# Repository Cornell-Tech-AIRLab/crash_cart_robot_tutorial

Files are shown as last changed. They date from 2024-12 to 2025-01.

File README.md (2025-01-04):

# CRASH-CART-ROBOT-TUTORIAL-HRI 🤖

Crash Cart Robot Tutorial 

Healthcare workers face many challenges during bedside care that impede team collaboration and often lead to poor patient outcomes. Robots have the potential to support medical decision-making, help identify medical errors, and deliver supplies to clinical teams in a timely manner. However, there is a lack of knowledge about using robots to support clinical team dynamics despite being used in surgery, healthcare operations, and other applications. This version of the crash cart is a "Wizard of Oz" robot, allowing us to explore the robot's interactions with healthcare workers without needing to spend the time and resources to program it to run autonomously.

<p align="center"> 
 
</p>

This tutorial provides step-by-step instructions to build a low-cost cart robot with multimodal feedback capabilities using speech, drawer lights, and alerts to indicate the location of relevant supplies and task reminders.

See the Tutorial on [YouTube](https://www.youtube.com/watch?v=EV-0HwNPJiY).

Taylor, A., Tanjim, T., Sack, M., Hirsch, M., Cheng, K., Ching, K., St. George, J., Roumen, T., Jung, M., Lee, H. (2025) “Rapidly Built Medical Crash Cart! Lessons Learned and Impacts on High-Stakes Team Collaboration in the Emergency Room.” In Proc. of the 20th Annual ACM/IEEE Conference on Human Robot Interaction (HRI).

Taylor, A., Tanjim, T, Cao, H., Lee, H. “Towards Collaborative Crash Cart Robots that Support Clinical Teamwork.” In Proc. of the 19th Annual ACM/IEEE Conference on Human-Robot Interaction (HRI). *2024 Best Paper Honorable Mention*

<p align="center"> 
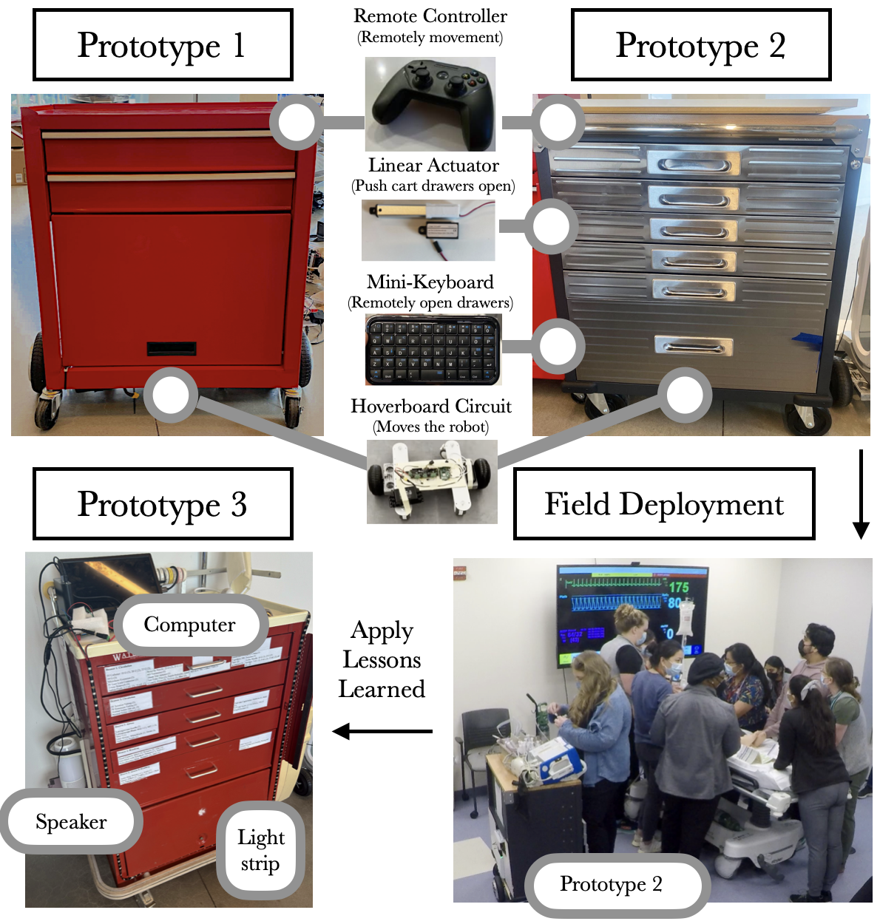
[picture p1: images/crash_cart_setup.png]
 

<b>Figure 1:</b> We built a series of teleoperated medical crash cart robots. Prototype 1 delivers supplies using a hoverboard circuit. Prototype 2 also delivers supplies, recommends supplies using drawer opening capabilities, and was deployed at a medical training event which revealed insights which led to the design of Prototype 3 that communicates recommendations and reminders using drawer lights, speech, and alerts.

</p>

## System Requirements
- Ubuntu 22.04.4 LTS (64-BIT)
- Python 3
- Robot Operating System 2 (Humble Distribution)

Contents: 
- [Introduction](#introduction) 
- [Materials and Supplies](#materials_supplies) 
- [Medical Crash Cart Robot Tutorial Steps](#medical_crash_cart_robot_tutorial_steps) 

## Introduction

Designing robots to support high-stakes teamwork in emergency settings presents unique challenges, including seamless integration into fast-paced environments, facilitating effective communication among team members, and adapting to rapidly changing situations. While tele-operated robots have been successfully used in high-stakes domains such as firefighting and space exploration, autonomous robots that aid high-stakes teamwork remain underexplored. To address this gap, we conducted a rapid prototyping process to develop a series of seemingly autonomous robot designed to assist clinical teams in the Emergency Room. We transformed a standard crash cart—which stores medical equipment and emergency supplies into a medical robotic crash cart (MCCR). The MCCR was valuated through field deployments to assess its impact on team workload and usability, identified taxonomies of failure, and refined the MCCR in collaboration with healthcare professionals. Our work advances the understanding of robot design for high-stakes, time-sensitive settings, providing insights into useful MCCR capabilities and considerations for effective human-robot collaboration. By publicly disseminating our MCCR tutorial, we hope to encourage HRI researchers to explore the design of robots for high-stakes teamwork.

You can use this bibtex to cite this work ([Taylor et al.](https://www.angeliquemtaylor.com/), 2025): 

``` 
@article{taylor_2025, 
author = {Taylor, A., Tanjim, T., Sack, M., Hirsch, M., Cheng, K., Ching, K., St. George, J., Roumen, T., Jung, M., Lee, H.}, 
title = {Rapidly Built Medical Crash Cart! Lessons Learned and Impacts on High-Stakes Team Collaboration in the Emergency Room.}, 
journal = {In Proc. of the ACM/IEEE Conference on Human Robot Interaction (HRI).}, 
year = {2025}
}
```

## Materials and Supplies

The parts list includes required supplies, price, quantity, and a link to a recommended source. You likely already own most items. The total cost of the supplies is $417.

The battery pack is optional; two wall outlets serves as an alternative. A Linux laptop computer is required.

<b>Table 1:</b> Equipment List

| Item                                     | Price         | Quantity      | URL           |
| ---------------------------------------- | ------------- | ------------- | ------------- |
| Raspberry Pi 4  (At least 4 GB)          | $55.00        | 1             | [Amazon](https://www.adafruit.com/product/4296)  |
| Individually addressable LED light strip | $17.99        | 1             | [Amazon](https://www.amazon.com/VISDOLL-Individually-Addressable-Flexible-Controller/dp/B0CPLS16JL/ref=sr_1_4_sspa?dib=eyJ2IjoiMSJ9.TsHmF-lRIoGBvYJC14yH76SiGa3kCQYP1z9MJw8sPbFHuxxiVUnvk2_fiU6mu656BQlq5KbTNHeb5_LumQcb0X0OYDHDtCJN_rwwuf5z-v3bWnlL3Cn5DcHwlOG_Mdx9sP37ajw4Ocg3C4Y7M3PlQIEP1Z9yZiresYGvkUS-f6ggZ01eL3WeGkKSrfykM7fkyz9CT9XE3tvYreNPs_VAVzMoKI3IduZyyRaUuZjE2DB9uh-IXvjCOFOB-BNWAV8X9jAMOFD0EhvupdupGt4MgoGf1YjCXj0orK1jpqZbRBg.J0vCnA8CnLhwxM7LNrnHI55PK87y2msPtlu4ZD3rIlE&dib_tag=se&hvadid=174243246868&hvdev=c&hvlocphy=9004331&hvnetw=g&hvqmt=e&hvrand=15947800415004845809&hvtargid=kwd-87871454332&hydadcr=29841_9846530&keywords=ws2812b%2Bled%2Bstrip&qid=1711394444&sr=8-4-spons&sp_csd=d2lkZ2V0TmFtZT1zcF9hdGY&th=1)  |
| Keyboard (Connects to USB A)             | $2.00         | 1             | [Amazon](https://www.staples.com/nxt-technologies-keyboard-black-nx60880/product_24517816?cid=ps:gs:dot:nb:pmax:transtech&gad_source=1&gclid=CjwKCAjwzIK1BhAuEiwAHQmU3t1JYTTmAYI_HaWwEZnc8uMsLGvTyHrGdflbFACUAaloaU-xJKD52BoCmyQQAvD_BwE)  |
| Mouse (Connects to USB A)                | $2.71         | 1             | [Amazon](https://www.staples.com/nxt-technologies-wireless-optical-usb-mouse-black-nx60885/product_24517815?cid=ps:gs:dot:nb:pmax:transtech&gad_source=1&gclid=CjwKCAjwzIK1BhAuEiwAHQmU3k907qJZk150g8lUc_bgR_WLXvN4HjRAyOvO-Sm72jIvwHWpznKH6xoCgBsQAvD_BwE)  |
| Monitor (With either a VGA or HDMI port) | $25.25        | 1             | [Amazon](https://www.aliexpress.us/item/3256807264652139.html?src=google&src=google&albch=shopping&acnt=708-803-3821&slnk=&plac=&mtctp=&albbt=Google_7_shopping&gclsrc=aw.ds&albagn=888888&ds_e_adid=&ds_e_matchtype=&ds_e_device=c&ds_e_network=x&ds_e_product_group_id=&ds_e_product_id=en3256807264652139&ds_e_product_merchant_id=552411188&ds_e_product_country=US&ds_e_product_language=en&ds_e_product_channel=online&ds_e_product_store_id=&ds_url_v=2&albcp=19623912707&albag=&isSmbAutoCall=false&needSmbHouyi=false&gad_source=1&gclid=Cj0KCQjw5ea1BhC6ARIsAEOG5pw0ThUU9ioUfy6q8Gpse0W5nCPYEZ5PL07aNTyMMek56Z9WtTKV-4waApLREALw_wcB&aff_fcid=041117238ac34ce9b29ae2ed38ab0a0f-1723474136729-08015-UneMJZVf&aff_fsk=UneMJZVf&aff_platform=aaf&sk=UneMJZVf&aff_trace_key=041117238ac34ce9b29ae2ed38ab0a0f-1723474136729-08015-UneMJZVf&terminal_id=415d44ae0b35443094f91ea630333c9f&afSmartRedirect=n&gatewayAdapt=glo2usa)  |
| Bluetooth speaker                        | $15.99        | 1             | [Amazon](https://www.amazon.com/Portable-Bluetooth-Wireless-Surround-Waterproof/dp/B08HKCH6HC/ref=asc_df_B08HKCH6HC/?tag=hyprod-20&linkCode=df0&hvadid=692875362841&hvpos=&hvnetw=g&hvrand=2035686413955776000&hvpone=&hvptwo=&hvqmt=&hvdev=c&hvdvcmdl=&hvlocint=&hvlocphy=9004331&hvtargid=pla-2281435180218&mcid=9e425a680a003b76bc8e3d1397160958&hvocijid=2035686413955776000-B08HKCH6HC-&hvexpln=73&gad_source=1&th=1)  |
| Male to female jumper wires              | $6.99         | 1             | [Amazon](https://www.amazon.com/Solderless-Multicolor-Electronic-Breadboard-Protoboard/dp/B09FP9M5J9/ref=sr_1_2_sspa?crid=285C9TEGW2OJE&dib=eyJ2IjoiMSJ9.6VrCXmlMYCYNvuTQX0vT18ycELHgXZXH9PN0oF4VWQdYk4psYj3UzBNkfVIU8OGZ4mi6Mo66XAKnZA7u0Idopb1NmCyKOZhnBhflIQloKcexdfN8Pxpzk5lSIB-XAtNZSnyTX9r9DEAhOVGiZ5ZN8bzyPb0FbIHclzaA-1-1LsXY3Z9E09I9gJSt13tY6p-ACQQbBvWMOF_940mtSjbySvwlDZREkQ4u65cgVEOfTxl9d-W6tyIptaniU_1eosEHJ_1_9GOZfSxJW9_Jn-fwQ8O1kt3PL9NwbfX-Acj7T38.bWZbX1JaxNVCQuquF9v3bd_YDqoABrhuUTLX3eYxoZk&dib_tag=se&keywords=long%2Bm%2Bto%2Bf%2Bjumper%2Bwire&qid=1722005738&s=industrial&sprefix=long%2Bm%2Bto%2Bf%2Bju%2Cindustrial%2C503&sr=1-2-spons&sp_csd=d2lkZ2V0TmFtZT1zcF9hdGY&th=1)  |
| Micro USB to HDMI or VGA                 | $7.99         | 1             | [Amazon](https://www.amazon.com/Converter-Compatible-Pictures-High-Definition-Monitor/dp/B09WMFKWYV/ref=asc_df_B09WMFKWYV/?tag=hyprod-20&linkCode=df0&hvadid=692875362841&hvpos=&hvnetw=g&hvrand=11251120234702158002&hvpone=&hvptwo=&hvqmt=&hvdev=c&hvdvcmdl=&hvlocint=&hvlocphy=9004331&hvtargid=pla-2281435177138&psc=1&mcid=906f684308503291bb8d74a65cd6fac0&hvocijid=11251120234702158002-B09WMFKWYV-&hvexpln=73&gad_source=1)  |
| USB C to power                           | $12.99        | 1             | [Amazon](https://www.amazon.com/Adapter-Charger-Charging-Compatible-Remarkable/dp/B09GYB2YG8/ref=asc_df_B09GYB2YG8/?tag=hyprod-20&linkCode=df0&hvadid=692875362841&hvpos=&hvnetw=g&hvrand=15632892786989388826&hvpone=&hvptwo=&hvqmt=&hvdev=c&hvdvcmdl=&hvlocint=&hvlocphy=9004331&hvtargid=pla-2281435182178&psc=1&mcid=8cc13fd8b3633d4c9d1ade48fa8707fa&hvocijid=15632892786989388826-B09GYB2YG8-&hvexpln=73&gad_source=1)  |
| Micro SD Card (At least 32 GB)           | $9.17         | 1             | [Amazon](https://www.amazon.com/dp/B073JWXGNT/ref=twister_B08CLNX58K?_encoding=UTF8&th=1)  |
| SD to USB adapter                        | $5.99         | 1             | [Amazon](https://www.amazon.com/Reader-Laptop-Windows-Chrome-RS-MMC/dp/B0C81FW814/ref=asc_df_B07MK99R14/?tag=hyprod-20&linkCode=df0&hvadid=692875362841&hvpos=&hvnetw=g&hvrand=5558208569019396501&hvpone=&hvptwo=&hvqmt=&hvdev=c&hvdvcmdl=&hvlocint=&hvlocphy=9004331&hvtargid=pla-2281435178778&mcid=b200ad31022538c49f855bc14aa1af93&hvocijid=5558208569019396501-B07MK99R14-&hvexpln=73&gad_source=1&th=1)  |
| Portable Power Station (optional)        | $249.99       | 1             | [Amazon](https://www.amazon.com/Anker-Portable-Generator-Traveling-Emergencies/dp/B0D62GMQ3F/ref=sr_1_1?crid=3OQSZ4QJ8UH6U&dib=eyJ2IjoiMSJ9.tGQ-J5haxYTAwL1awybF7r5b77QzjHUV5L4DpdkEKx9327o1Ri0o_fAo0fHeau_H_mCO-QfKyUxtNJJXKOpWLSvHvortJRIqT5scaOl5mlmgb0ho0jWMixqvxFlyN4EEjfWuSRUjDf8qWkElX4z0CoGpGwvA4_LAjuRklcHMRCFmmos63CCWAYLKFk4nqihG.nzRxaNY_JeZWl6dEtIdO0v09trXHNOOJdBqo8NcMjJU&dib_tag=se&keywords=anker+solux+c300x&qid=1734398531&sr=8-1)  |
| Scissors       | $4.24       | 1             | [Amazon](https://www.amazon.com/Scotch-1448-Precision-Scissor-8-Inches/dp/B001BKHHGS/ref=sr_1_5?crid=3V6SGIOQY7GU7&dib=eyJ2IjoiMSJ9.AjnComGyJnnJDRxxKFsxrNZHsMajCroUmd9qmX9nwIOeL8NUWILLhf7m7GxhVHXJnSHxpMeviTaEr2LnuPAxmw40hzl5Rdf_Owijw15Fy58SLyvQSLHSMel_WyEC4AQZjH3Wt3JMTi1D037q23B5Cp1LPqoWigxGkm8_nxsQEbk3pv5QtdriHM7wb_MSsVRWeJwYsnVV2mQhtSZmZ_oRn224Hzd6j-kkbbp2dRziO-LeHCFQFuRcWnOHuxAPROuZ2WCSZpSRmqLKDERhPR45x7LS81Nw6ncDYR1A48UJBUrHKtb-hRQ5I1Oo6R-ewswABJY6XRysK8yfr27H418VAKIqyyR3SABpj_s_BKoh9HcsGG-t7I9cEZCXVo_tpq80HNKd30ano7Ue8xTeSEQm9efUqQki64hn65fJhfFTHbI2lMVCrg_3kpbujX3iycB5.C85nwNh6hfaxJT_z_jb20ZgRAuvMlOfdWmmTRzfnOW0&dib_tag=se&keywords=scissors&qid=1735255473&sprefix=scissors%2Caps%2C189&sr=8-5)  |

## Medical Crash Cart Robot Tutorial Steps

### Step 1: Set up micro SD card (12 minutes)

<b>1.1</b> Download the version of the Raspberry Pi Imager application compatible with your computer https://www.raspberrypi.com/software/.

<b>1.2</b> Insert the micro SD card into your computer directly or through an adapter.

<b>1.3</b> Open the Imager and fill out the following options:

<b>1.4</b> Raspberry Pi Device: Raspberry Pi 4
- Operating System: Other general-purpose OS → Ubuntu → UBUNTU DESKTOP 22.04.4 LTS (64-BIT)
- Storage: Your SD Card reader

<p align="center"> 
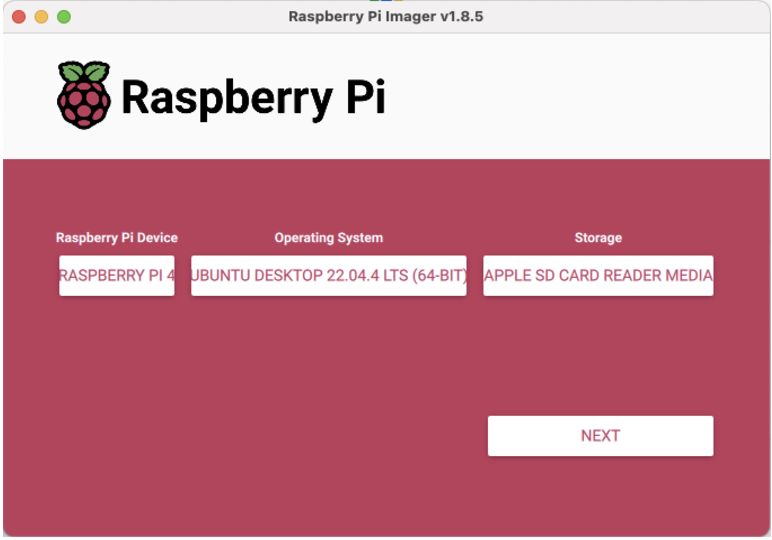
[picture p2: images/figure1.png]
 
</p>

<p align="center"> 
<b>Figure 2:</b> Set up a micro-SD card for Raspberry PI 4 using Imager application.
</p>

<b>1.5</b> Click “NEXT” and wait around eight minutes for the imager to write successfully.

<b>1.6</b> Once complete, safely remove the card. 

<b>1.7</b> Insert the microSD card into the Raspberry Pi with its metal bits facing the bottom of the Pi.

### Step 2: Attach the LED strip to the cart (10 minutes)

<b>2.1</b> Peel some of the adhesive back off of the LED strip and start attaching it to the cart. If the adhesive isn’t strong enough, you may need glue or tape.

<b>2.2</b> Make sure around two LEDs correspond nicely to each drawer to make it easier for the cart to give clear instructions regarding which drawer a user should select.

If struggling to align the LEDs with the drawers, gently pinch the LEDs as shown below to adjust their positions.

<p align="center"> 
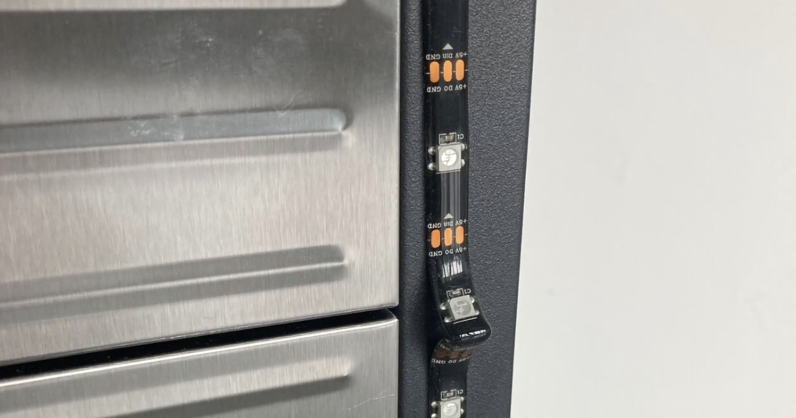
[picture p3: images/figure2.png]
 
</p>

<p align="center"> 
<b>Figure 2:</b> Attach LED lights to the cart.
</p>

<b>2.3</b> Once attached to one side, curve the strip under the cart, run it along the bottom, and have it curve up to the other side.

<b>2.4</b> When attaching the strip to the other side, make sure to keep the lighting symmetrical. Mirror the positioning of each individual LED to ensure level lighting across the cart. It should look like this:

<p align="center"> 
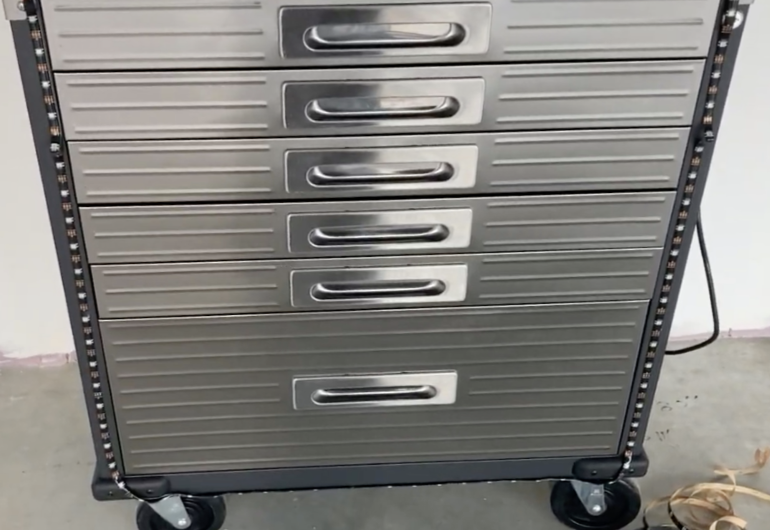
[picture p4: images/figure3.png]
 
</p>

<p align="center"> 
<b>Figure 3:</b> LED lights installed to ensure uniform lighting across the cart.
</p>

<b>2.5</b> Once you’ve lined up the LEDs, cut the excess on the white line with the copper strips.

### Step 3: Connect Electronics (10 minutes)

<b>3.1</b> Make sure you put in the Micro SD card before you plug the Pi into the outlet!

<b>General wiring</b>

<b>3.2</b> Connect your monitor to the outlet using the female/male plug cable.

<b>3.3</b> Connect your Raspberry Pi to the outlet using the mini USB/male plug cable.

<b>3.4</b> Connect your monitor to the Raspberry Pi using either your HDMI/micro HDMI cable or VGA/micro HDMI cable, depending on which port your monitor contains.

<b>3.5</b> Connect your keyboard to the Raspberry Pi using its wire to USB A.

<b>3.6</b> Connect your mouse to the Raspberry Pi using its wire to USB A.

<b>3.7</b> For the jumper wires:
- Connect the red wire to a 5V power pin (Pin #2 or #4 on a Pi 4)
- Connect the black wire to a ground pin (Pin #6 on a Pi 4)
- Connect the green wire to the GPIO 18 pin (Pin #12 on a Pi 4)

<p align="center"> 
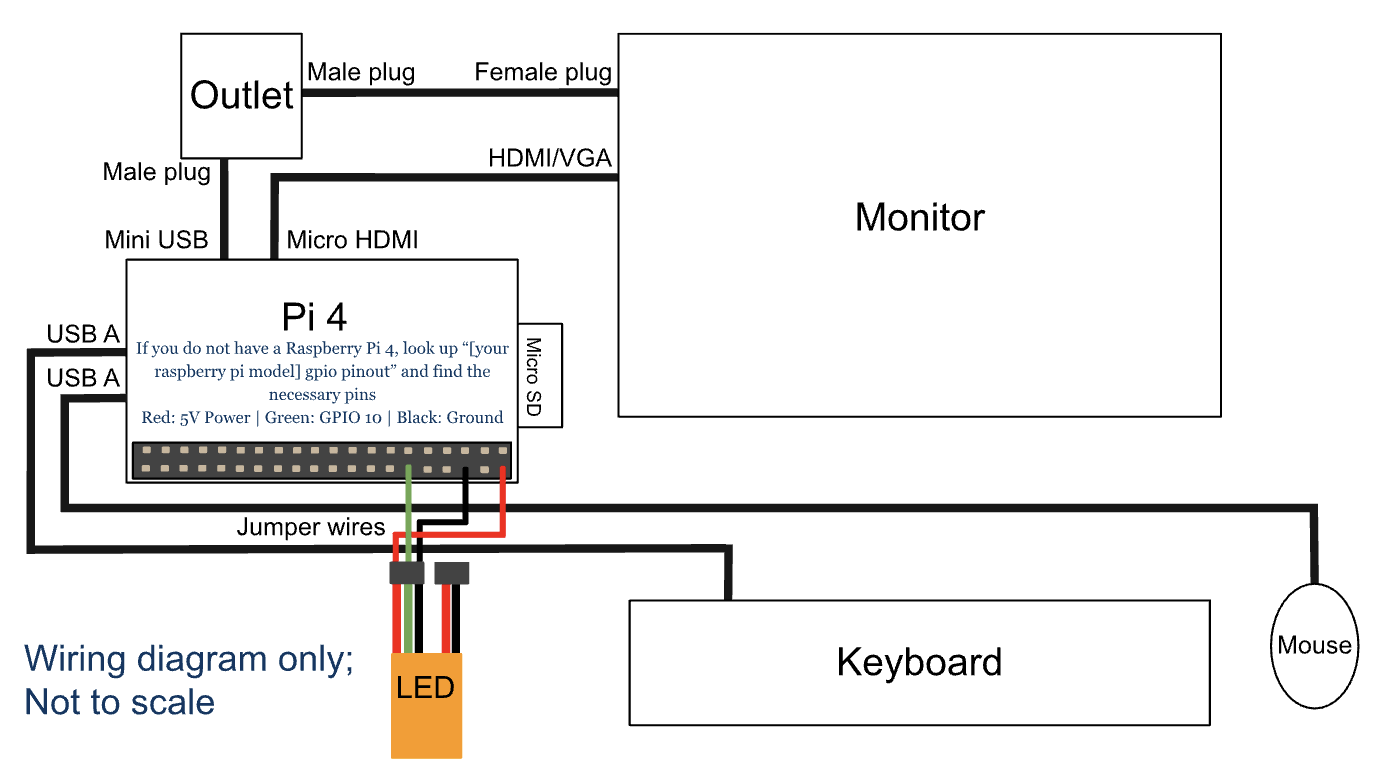
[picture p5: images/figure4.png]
 
</p>

<p align="center"> 
<b>Figure 4:</b> Electronic wiring connections for Raspberry Pi 4 with monitor, keyboard, mouse, and LED using appropriate wires and ports.
</p>

### Step 4: Boot the Raspberry Pi (12 minutes)

<b>4.1</b> Once the monitor is connected to the RPi4 to a power outlet, make sure its input is switched to either VGA or HDMI, depending on the port you connected the Pi to.

<b>4.2</b> The Pi should boot with a rainbow screen, then a black one with some white text in the top left corner, and then the Ubuntu loading screen. It should then open to a really cute jellyfish background.

<b>4.3</b> Wait a second, then the screen should start to ask you about your settings.

<b>4.4</b> Enter your desired settings, and make sure to connect to wifi now to save time later.

<b>4.5</b> Submit your choices, then wait for the system to configure. This may take some time.

<b>4.6</b> The computer should then reboot, allowing you to sign in.

<b>4.7</b> When it opens, system program problems and internal errors may pop up, you can ignore those messages.

<b>4.8</b> You can skip through the setup instructions, and once you’re done, congratulations! You’ve set up an Ubuntu operating system on a Raspberry Pi.

### Step 5: Download necessary files (6 minutes)

<b>5.1</b> Open a web browser (such as Firefox) to access the project GitHub repository on your monitor: https://github.com/Cornell-Tech-AIRLab/crash_cart_robot_tutorial

<b>5.2</b> Press the green “Code” dropdown button.

<p align="center"> 
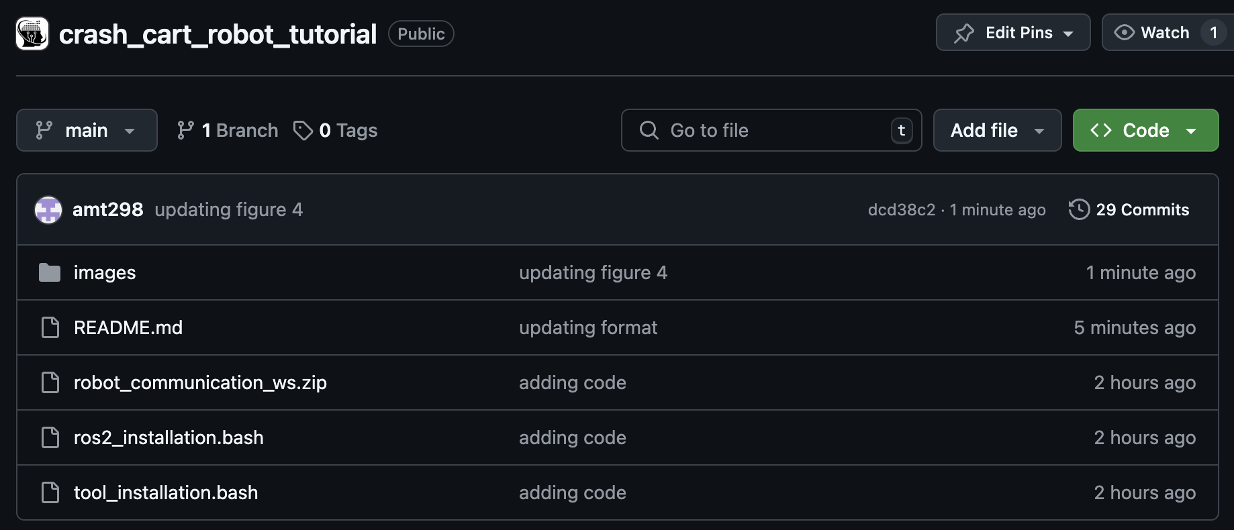
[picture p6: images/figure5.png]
 
</p>

<p align="center"> 
<b>Figure 5:</b> Downloading necessary files from the Github repository.
</p>

<b>5.3</b> Click the “Download ZIP” button and wait for it to download.

<b>5.4</b> Open the zip files, then right-click the file and press “Extract Here.”

<p align="center"> 
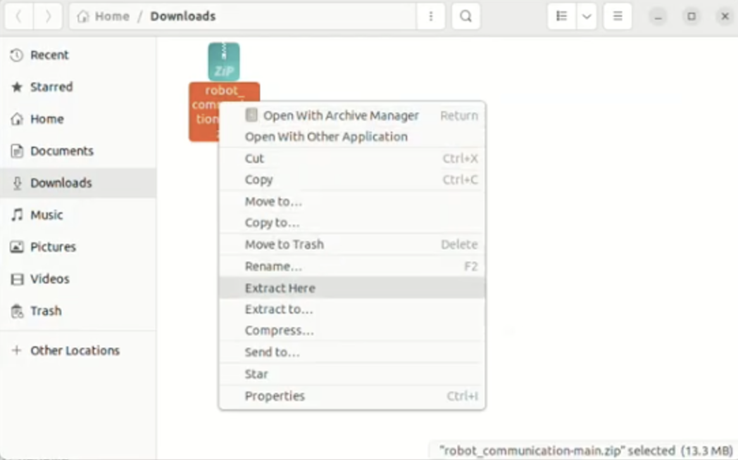
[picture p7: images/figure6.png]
 
</p>

<p align="center"> 
<b>Figure 6:</b> File extraction of the GitHub Repository.
</p>

<b>5.5</b> Open the resulting folder and right-click the robot_communication_ws zip file and press “Extract Here.”

<b>5.6</b> Make sure to wait for the extracted successfully popup, as not doing so will cause future issues. Then, drag the “robot_communication_ws” folder along with the “ros2_installation.bash” and “tool_installation.bash” files to “Home.”

<b>5.7</b> Double-check check that everything was moved properly to the ‘Home’ folder.

<p align="center"> 
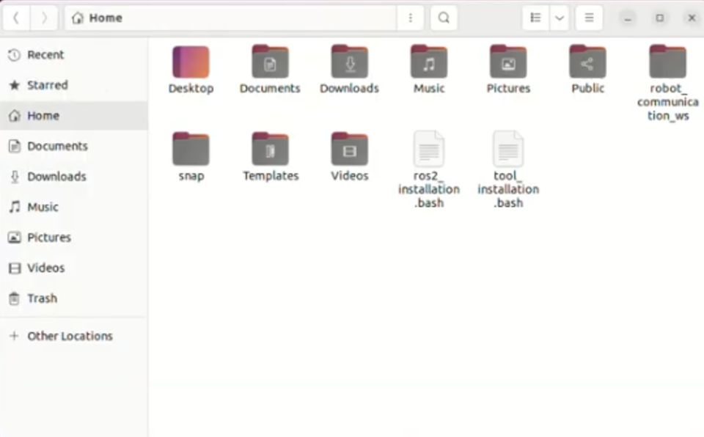
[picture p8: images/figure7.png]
 
</p>

<p align="center"> 
<b>Figure 7:</b> Bash file setup.
</p>

### Step 6: Download Robot Operating System 2 (55 min)

<b>6.1</b> Go to the bottom left of your screen and view your applications.

<b>6.2</b> Click “Terminal” to open a terminal window.

<b>6.3</b> Right-click the Terminal icon on the left side menu and click “Add to favorites” for easy access in the future.

<b>6.4</b> Type in the following command and press enter: 
```
bash ros2_installation.bash
```

This will install Robot Operating System 2, or ROS2. This will let us easily control the robot

<b>6.6</b> Then enter your monitor’s password. Your keyboard is typing, even though characters won’t appear.

<b>6.7</b> Let the program run. Use the next 50 minutes of loading time to watch cars pass by, contemplate existence, or take a nap.

<b>6.8</b> Make sure to check the screen every so often, though, as it will ask you to press enter or enter a capital Y for permissions a few times.

<b>6.9</b> Once it finishes running, it’s time to test the fruits of your hard work! Open two new terminal windows and close the old one.

<b>6.10</b> Enter the following commands in the terminal:
```
source /opt/ros/humble/setup.bash
ros2 run demo_nodes_cpp talker
```

<b>6.11</b> Then enter these into another terminal:
```
source /opt/ros/humble/setup.bash
ros2 run demo_nodes_py listener
```

<b>6.12</b> If the first window is saying that it's publishing ‘Hello World’ and the second says it’s hearing ‘Hello worlds, yippee!’ You’ve installed ROS2 successfully :)

If not, try googling your error message to debug.

### Step 7: Install necessary tools (6 min)

<b>7.1</b> Open a new terminal window and enter the following. This will install the tools necessary for the program to run properly. Wait around six minutes for it to finish running:
```
bash tool_installation.bash
```

### Step 8: Test and edit light code for compatibility (25 minutes)

<b>8.1</b> Open a new terminal window and run the following to run the light node
```
source /opt/ros/humble/setup.bash
colcon build --symlink-install
cd robot_communication_ws
source install/setup.bash
ros2 run light_pkg light_node
```

<b>8.2</b> Try pressing a couple of the buttons and watch the lights on the carts flash. You may have noticed that the buttons don’t light the correct LEDs. If this is the case, you must edit the code to be compatible with your cart.

<b>8.3</b> Go to your files, follow this file path, and open the py file: Home → robot_communication_ws → source → light_pkg → light_pkg → light_node.py

<b>8.4</b> Open a new terminal window and rerun the module by entering the following (quick tip, if you press the up arrow you can the following commands in your history and can enter them like that to make it easier):
```
source /opt/ros/humble/setup.bash
colcon build --symlink-install
cd robot_communication_ws
source install/setup.bash
ros2 run light_pkg light_node
```

<b>8.5</b> Once you’ve run the program, click the first button and watch to see which lights flash. If only one pair lights up, the program is trying to light LEDs we’ve cut off.

<b>8.6</b> Go to the portion of the light_node code shown below. 

<p align="center"> 
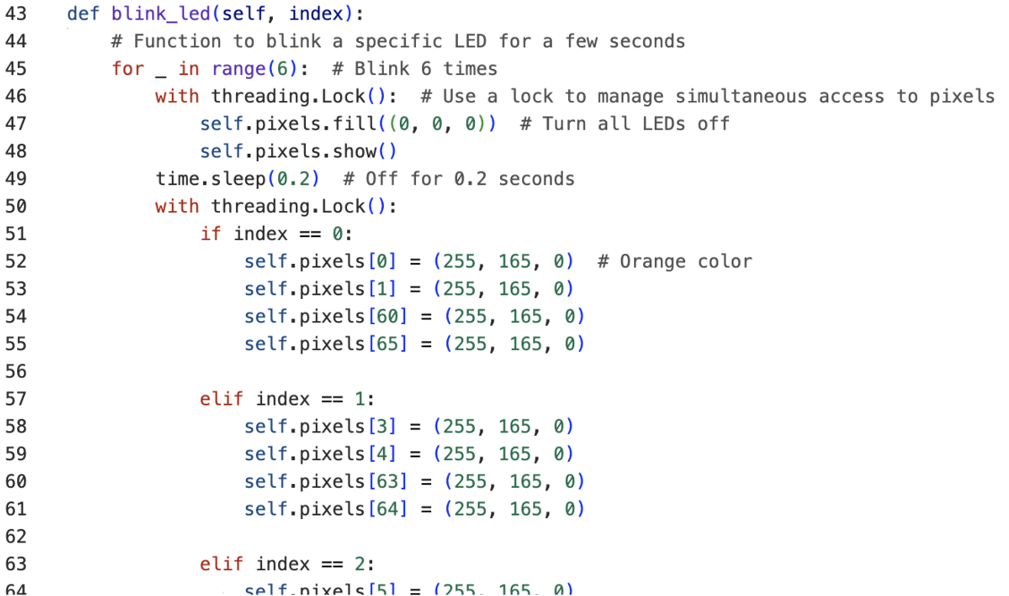
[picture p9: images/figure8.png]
 
</p>

<p align="center"> 
<b>Figure 8:</b> Code snippet for modifying RGB values, LED colors, and corresponding LED lights.  
</p>

<b>8.7</b> Each four-line section of code corresponds to one button on the pop-up, one drawer that needs to be lit. Editing the number in the square brackets for the first section will change which LED is lit when the first button is pressed. Increasing the number will make the lit LED further from the end with the wires, decreasing it will make the LED closer to that end.

<b>8.8</b> Edit the number, press the save button at the top of the code’s window, press Control C in the terminal window to stop the program, open a new window, then rerun the node:
```
source /opt/ros/humble/setup.bash
cd robot_communication_ws
source install/setup.bash
ros2 run light_pkg light_node
```

<b>8.9</b> Look to see which LEDs light up now. Is it still too far one way? Or maybe now too far the other way? Repeat step h until each button properly lights a different drawer from both sides with the final two buttons flashing all the lights. This should take around 15 minutes.

<p align="center"> 
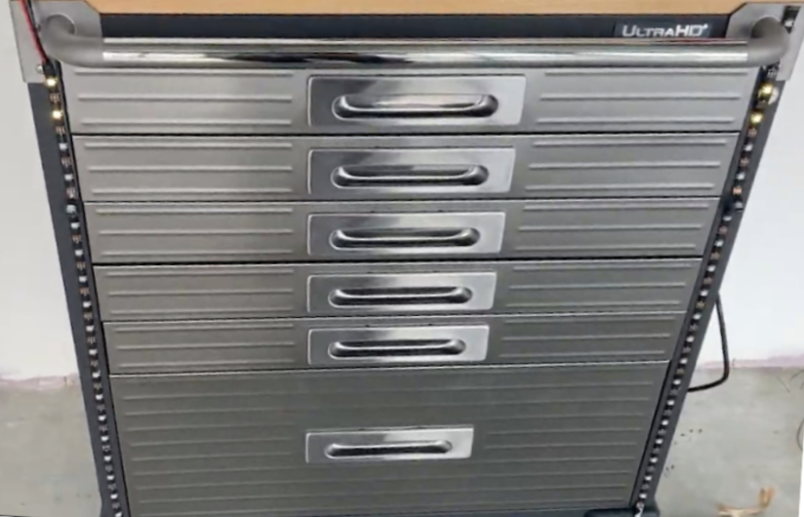
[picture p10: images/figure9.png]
 
</p>

<p align="center"> 
<b>Figure 9:</b> LED lights installed across the mobile crash cart.
</p>

### Step 9: Connect the Bluetooth speaker (1 minute)

<b>9.1</b> Make sure your speaker is turned on and in range.

<b>9.2</b> Go to the top right corner of the screen. Click “Bluetooth On”, then “Bluetooth Settings”. Once your speaker pops up, click its name and switch on the connection.

### Step 10: Test the alert module (1 minute)

<b>10.1</b>  Open a terminal and run the following commands to test the alert module:
```
cd robot_communication_ws
source install/setup.bash
ros2 run alert_pkg alert_node
```

<b>10.2</b> Click the buttons, and you should hear beeping!

### Step 11: Test the dialogue module (1 minute)

<b>11.1</b> Open a terminal and run the following commands to test the dialogue module:
```
cd robot_communication_ws
source install/setup.bash
ros2 run dialogue_pkg dialogue_node
```

<b>11.2</b> Click the buttons, and you should hear the robot’s dialogue.

## Congratulations! You are now the proud owner of a robotic crash cart.

## Contributing

Contributions are what make the open source community such an amazing place to learn, inspire, and create. Any contributions you make are greatly appreciated.

Fork the repo and create a pull request to improve the tutorial. You can also simply open an issue with the tag "enhancement". Don't forget to give the project a star! Thanks again!
- Fork the Project
- Create your Feature Branch (git checkout -b feature/AmazingFeature)
- Commit your Changes (git commit -m 'Add some AmazingFeature')
- Push to the Branch (git push origin feature/AmazingFeature)
- Open a Pull Request

## Further Issues and questions ❓ 

If you have issues or questions, don't hesitate to contact:

- Anaiya Z. Badi (anaiya.badi@gmail.com)
- Tauhid Tanjim (tt485@cornell.edu)
- Angelique M. Taylor (amt298@cornell.edu)

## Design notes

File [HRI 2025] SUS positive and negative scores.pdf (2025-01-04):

Supplemental Materials

Results

System Usability Scale

Positive SUS questions assess aspects such as ease of use, functionality integration, and user confidence. Observations indicate that questions like "The system was easy to use" and "The functions in this system were well integrated" received moderate scores, reflecting general satisfaction with these aspects. However, lower scores for "I felt very confident using the system" suggest that while users found the robot crash cart functional, they lacked assurance during use. Additionally, relatively low scores for "I think that I would like to use this system frequently" indicate limited perceived usefulness or appeal for repeated use.

In contrast, the negative SUS questions highlight areas where the robot crash cart struggles in usability. High scores for "I found the system unnecessarily complex" and "I needed to learn a lot of things before I could get going" reflect significant challenges in robot crash cart intuitiveness and initial onboarding, while higher scores for "I think that I would need the support of a technical person to use this system" suggest that users may require external assistance to effectively navigate the robot crash cart. Moreover, moderate scores for "I found the system very cumbersome to use" indicate usability issues that detract from user efficiency and satisfaction when using the robot crash cart.

The positive SUS questions (see Figure 1), which focus on usability of the robot crash cart, show a range of average scores between 2 and 3. The lowest average score was 2.0 for "I felt very confident using the system" (Q9). On the other hand, the highest average score was 3.0 for "I would imagine that most people would learn to use this system very quickly" (Q7), suggesting that users believe the robot crash cart’s learning curve is manageable for most people. The standard deviations (STD) vary, with Q1 ("I think that I would like to use this system frequently") showing the highest STD at 1.33, while Q9 ("I felt very confident using the system") has the lowest STD at 0.87. Overall, the positive scores reflect moderate satisfaction but highlight a lack of confidence in using the robot crash cart.

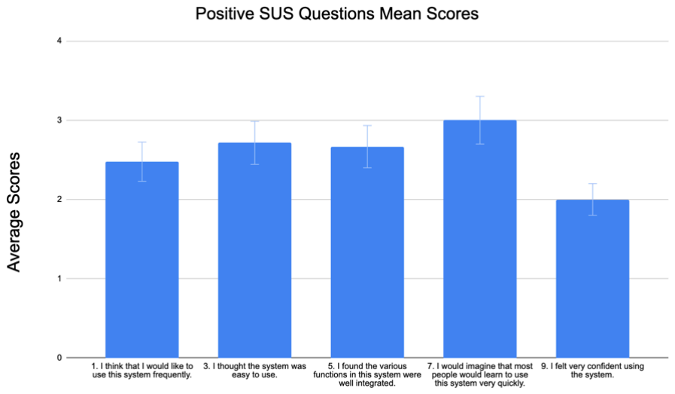
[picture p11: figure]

Figure 1: Positive SUS Questions Mean Scores

In comparison, the negative scores (see Figure 2) were generally higher than the positive scores, suggesting more dissatisfaction than satisfaction in usability among users. The negative SUS questions (see Figure 2), which assess areas of complexity, inconsistency, and difficulty, resulted in averages ranging from 2.76 to 3.71. The highest average score was 3.71 for "I needed to learn a lot of things before I could get going with this system" (Q10), indicating a strong perception that the robot crash cart requires significant improvement in terms of user training before interacting with the robot. In contrast, the lowest average score was 2.76 for "I found the system unnecessarily complex" (Q2), suggesting that while the robot crash cart is perceived as complex, it may not be the most pressing issue. These questions resulted in the highest and lowest STDs which are relatively similar, ranging from 0.93 to 1.15. Overall, the negative scores highlight difficulties with usability and training users to use the robot crash cart as a learning tool. The gap between the highest negative score (3.71) and the lowest positive score (2.0) emphasizes that users struggled significantly with the robot crash cart preparation and confidence which are significant usability concerns.

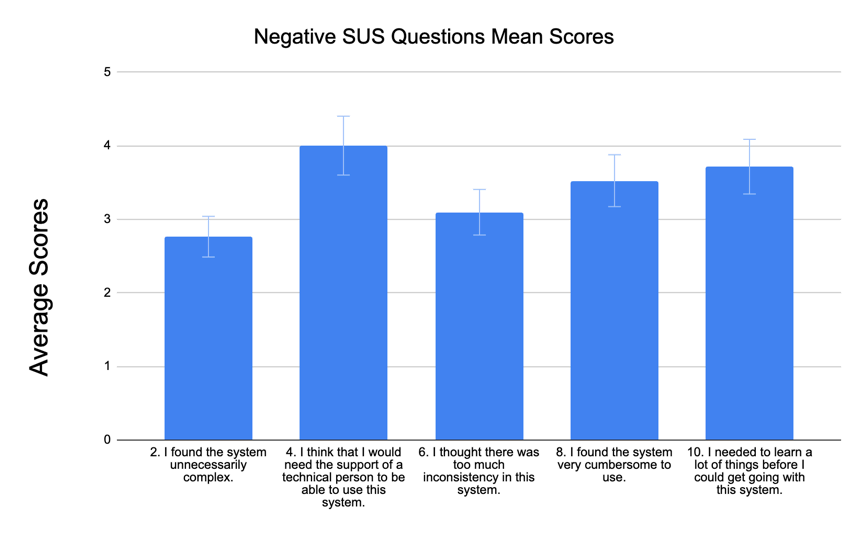
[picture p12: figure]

Figure 2: Negative SUS Questions Mean Scores

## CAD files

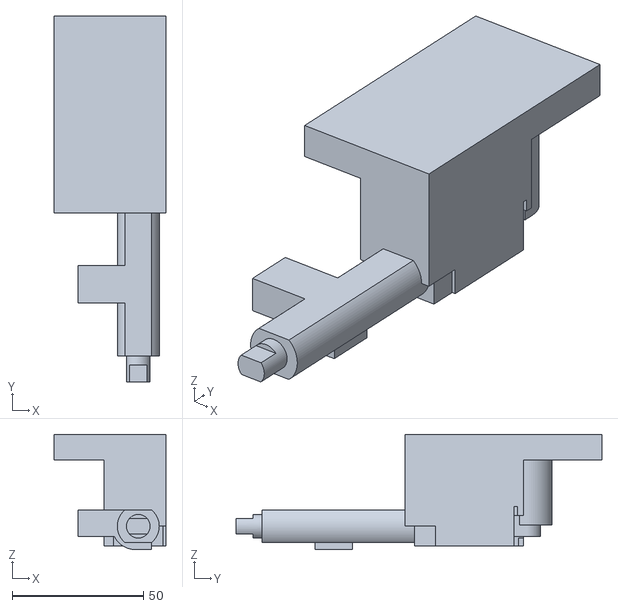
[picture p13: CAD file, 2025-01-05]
linear_actuator_casing/Actuator Casing.stl
42.6 x 139.5 x 43.9

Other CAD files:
linear_actuator_casing/Actuator Casing.f3d

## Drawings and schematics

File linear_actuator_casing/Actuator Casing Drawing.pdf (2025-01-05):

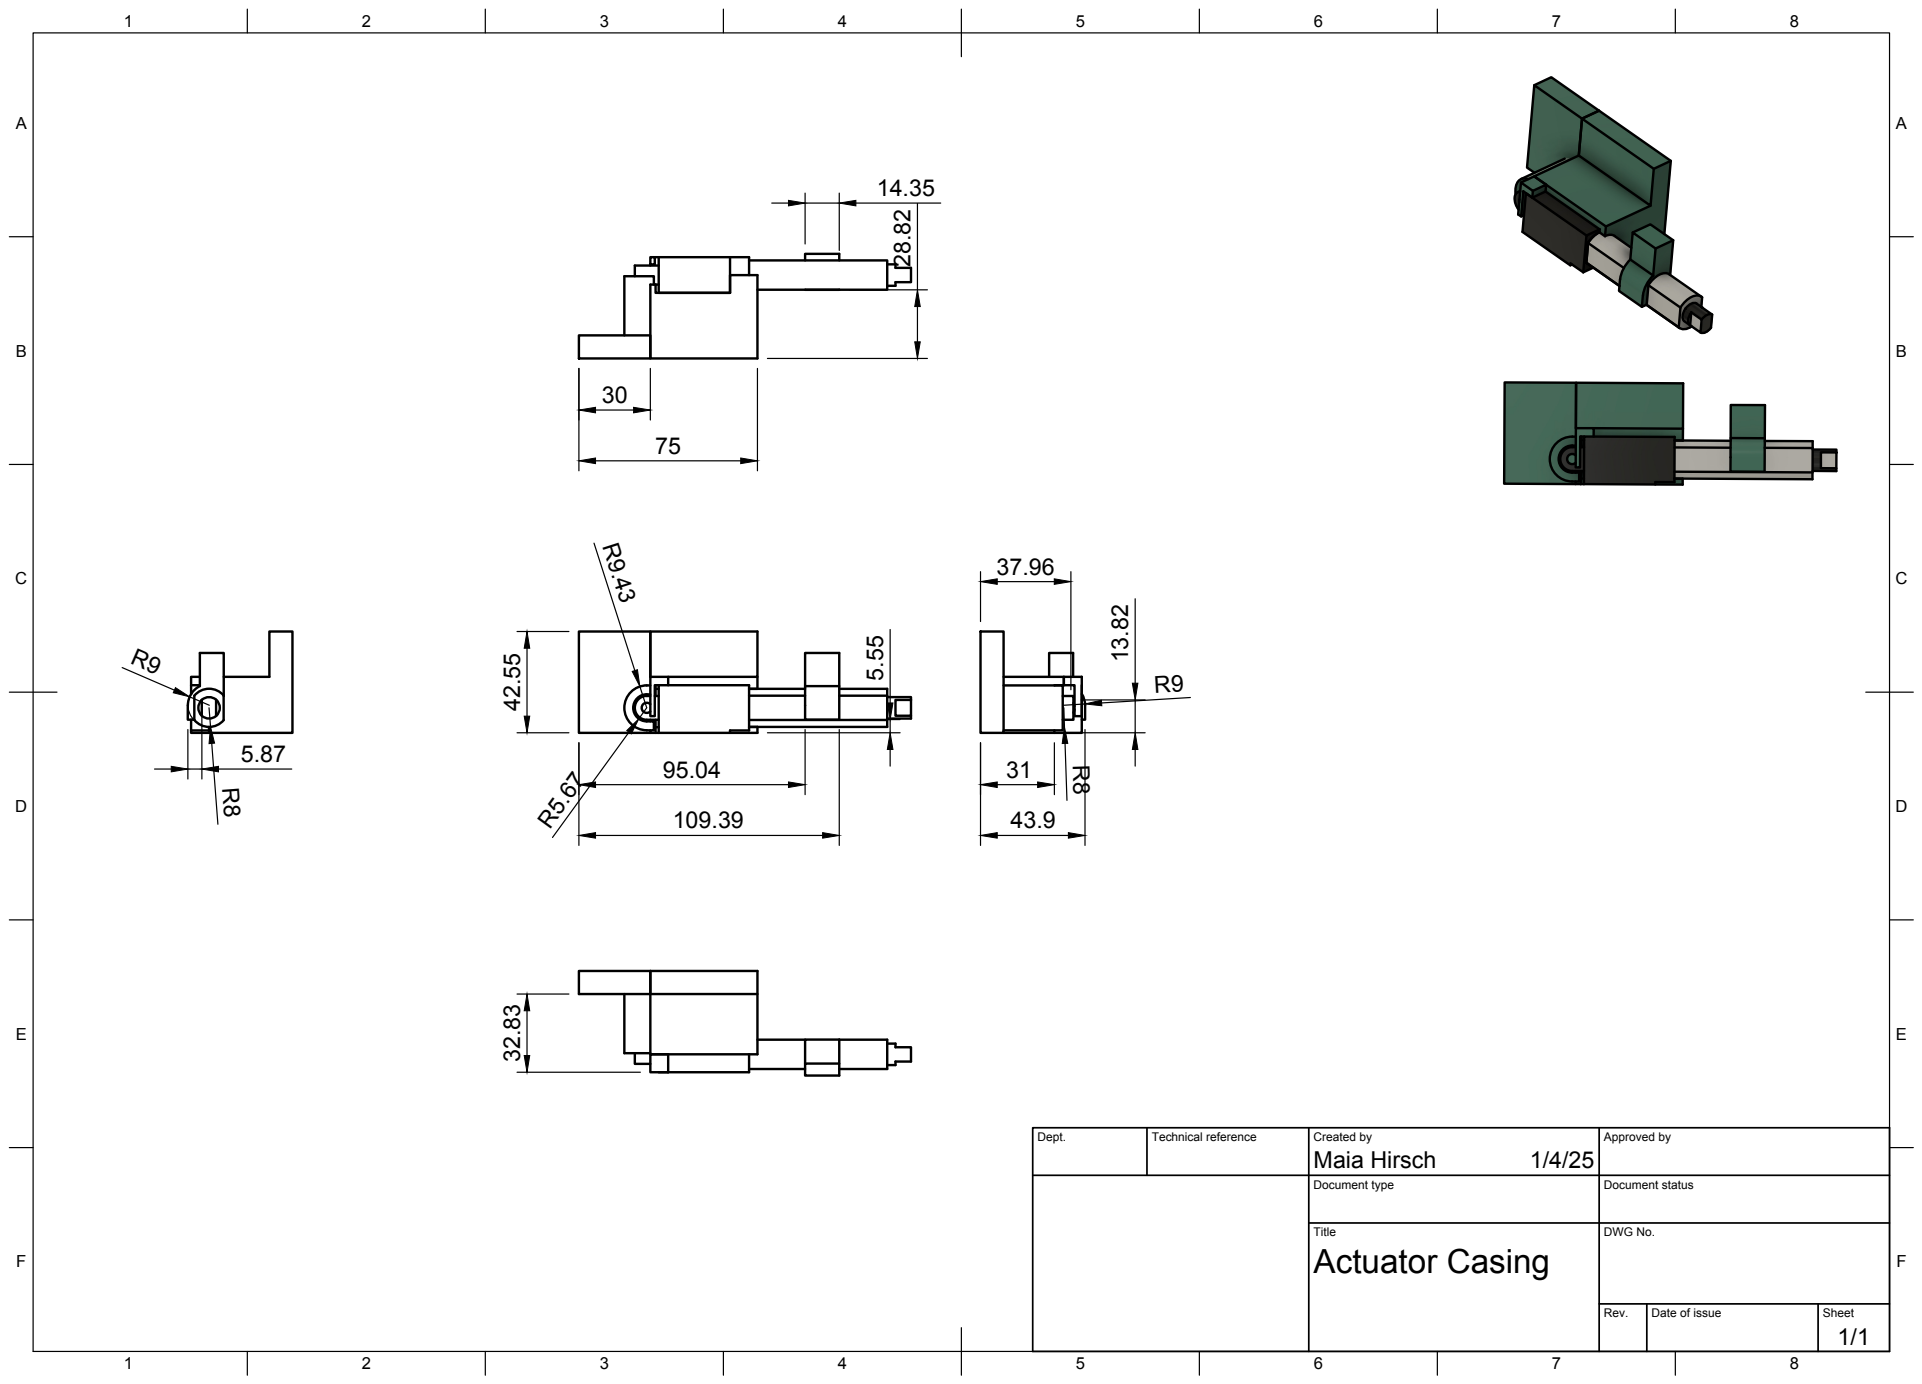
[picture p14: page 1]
Title; DWG No.; Rev.; Date of issue; Sheet; Actuator Casing; Maia Hirsch 42.55

Dept. | Technical reference | Created by 1/4/25 | Approved by

Document type | Document status
